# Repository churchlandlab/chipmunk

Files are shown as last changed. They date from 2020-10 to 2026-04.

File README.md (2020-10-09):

# chipmunk

Freely moving auditory and visual discrimination task for mice (adapted from Raposo et al. 2012)

### Introduction

This repo contains code, setup description, assembly instructions and parts design to build a freely moving behavior setup.

The task is a visual and/or auditory accumulation of evidence task. The stimuli is stochastic ticks and/or flashes.

### Description of the setup

[partslist here](partslist.xlsx)
	
There should be a picture here.
	
Here goes a description in words.
	
3d parts for building the setup are in the **custom_parts/3d** folder.
	
The walls are laser cut from *pololu* and the drawings are in the **custom_parts/enclosure**
	
The visual and auditory stimuli printed circuit boards are [here](https://github.com/churchlandlab/SpatialSparrow/tree/dev-couto/pcb/led_panel_split) and can be ordered from *SeeedStudio*.
	
### Software instalation

#### Bpod gen 2

Install Bpod from the repository [here](https://github.com/sanworks/Bpod_Gen2). This was tested with commit `329bd9e`.

### chipmunk task
Clone the repository to `Bpod Local/Protocols`. If you make changes; create a branch and remember to commit changes regularly.

### Calibration 

##### Stimuli

The visual stimuli LEDs response curve should have a plot here.

The auditory speaker response curves were measured with X microphone and a picture should be here.

This needs to be done for every rig? Stored somewhere? Where?

#### Water reward size

Use BPOD to do this. An explanation should be here.

### Behavior monitoring

Cameras wiring for sync is done like this. (Needs diagram.)

Use cameras that have GPIO connections like the FLIR Chamaeleon 3. 
On the Chamaeleon 3 USB you can use the Purple wire (GPIO 2). Connect to BPod to signal trial start and/or end.  To sync multiple cameras use the Green wire and set one of the cameras as master (It is smart to use the same sampling rate). 

Cameras should be set like the following picture. This gives the tracking results with DeepLabCut below (figure).

### Training strategy

Training has 3 phases:

1. Habituation - description of what happens in this phase. How long it lasts. When it ends.

2. Training phase - during these phase mice do the task but only with easy stimuli. This takes around 4 weeks.

3. Testing/experiment phase - mice are now considered experts and difficult stimuli are introduced. Mice perform X above chance.
	
Figure of performance, accross days. Code to produce this figure in the **notebooks** folder

### TODO

Arena size is 20x20cm. An additional chamber can attached to hold an observer.
 
1. walls and floor - laser cut drawings there is an additional 3d part to connect the walls - use transparent red acrylic #2423 from *Pololu*, 6mm. Where can we find small hinges?
2. test the stimuli and put the results in a figure here somewhere. With a description of how to do this.
3. Do we use a sound card?? What the latency? Fixed? How fixed?
4. 3d parts for the ports 2 - adapt the design so that head gear on a mouse is not does not touch the port during licking. Can we do this just with a spout and capacitive sensing?
5. What's in the current port PCB, where the drawing?
6. try different training strategies. Find the best strategy. What the best way to get multimodal enhancement? What is the best loudness and visual saliency? 

Most of these can be done in parallel, some can't. Version 1 can be rough for most of these (we can use code and audio from MudSkipper2 for now.)

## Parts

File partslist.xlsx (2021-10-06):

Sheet: Walls and floor
Part name | Supplier | Catalog number | Price | # parts per rig | Where does it go?
Chipmunk enclosure | Custom pieces |  | 390 | 1
1'' optical post | Thorlabs | TR1 | 4.88 | 3 | Pole to anchor camera to ground plate
8'' optical post | Thorlabs | TR8 | 8.79 | 4 | Legs attaching the ground plate to the floor
2'' optical post | Thorlabs | TR2 | 5.38 | 4 | Camera positioning, 1 each on the groud plate, 2 for the observer side view
1/4"-20 Stainless Setscrew, 1/2", pack of 25 | Thorlabs | SS25S050 | 6.11 | 1 (6 needed) | Fixing the legs and camera posts to the ground plate
Cap screw 8/32 x 1/2'', pack of 50 | Thorlabs | SH8S050 | 7.19 | 1 (4 needed) | Fixing the legs to the floor
Cap screw 1/4''-20 x 3/8'', pack of 50 | Thorlabs | SH8S038 | 6.93 | 1 (2 needed) | Attaching dovetail optical rail to floor and 2'' post to dovetail carrier
Cap screw 8/32 x 1/4'', pack of 50 | Thorlabs | SH8S025 | 6.65 | 1 (2 needed) | Hold demonstrator front and right side wall together with rubber band
Rubber band |  |  |  | 1 | Hold demonstrator front and right side wall together with rubber band
Right-Angle Clamp for Ø1/2" Posts | Thorlabs | RA90/M | 10.05 | 4 | Camera positioning
Dovetail optical rail |  | RLA 0600 | 45.72 | 1 | Observer side view camera adjustment
Dovetail carrier, 1/4'' | Thorlabs | RC1 | 26.94 | 1 | Observer side view camera adjustment
Warm white LED strip | Amazon | B08CDJGRLQ | 36.99 | 1 (~25 cm needed) | Booth lighting

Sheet: Behavioral control
Part name | Supplier | Catalog number | Price | # parts per rig | Where does it go?
Bpod 2 | Sanworks | 1024 | 865 | 1 | Control behavior
Custom nose poke with 8/32 thread on the back |  |  |  | 4 | Nose poke body
19 mm inner spacing ring, 38.2 mm inner diameter (for poke) |  |  |  | 4 | Spacer at the inside of the cage
10 mm outer spacing ring, 38.2 mm inner diameter (for poke) |  |  |  | 4 | Spacer at the outside of the cage
spacer plate |  |  |  | 4 | Additional spacer plate
Nose poke PCB with beam break and LEDS |  |  |  | 4 | Control of beam breaks, LEDs and solenoid valves
Cap screw 8/32 x 1'', pack of 50 | Thorlabs | SH8S100 | 8.27 | 1 (8 needed) | Attaches nose poke PCB to the poke on the outside of the cage
Washer #8, pack of 100 | Thorlabs | W8S038 | 3.59 | 1 (8 needed) | Between screw head and PCB
Haxagonal nylon standoff for 8/32 screws, pack of 10 | Grainger | 3XYN9 | 2.92 | 1 (8 needded) | To attach PCB above the spacer plate
Teensy 3.2 | Adafruit | 2756 | 19.95 | 1 | Control of the beam break for the observer deck
Perma-proto half-sized breadboard | Adafruit | P1609 | 4.5 | 1 | Bread board for observer deck control
Teensy shield | Sanworks | 1023 | 32 | 1 | Connect teensy to Bpod
3 mm infrared LED | Mouser | 696-OED-EL-8L | 0.4 | 1 | Observer deck beam break
3 mm photodiode | Mouser | 710-1540031EC4590 | 0.65 | 1 | Observer deck beam break
47 Ohm resistor, 1/4 W | Mouser | 603-CFR-25JT-52-47R | 0.1 | 1 | Resistor between 5V input and LED
1 MOhm resistor, 1/4 W | Mouser | 588-OK1055E-R52 | 0.13 | 1 | Resistor between diode readout and ground
Solenoid valve | The Lee Company | LHDA1233115H |  | 4 | Control of water dispensing
Silicone valve cap, pack of 50 | Amazon | B08H5TT689 | 5.99 | 1 (4 needed) | Control of water dispensing
Silicone tubing | Grainger | 9WDF5 | 76.3 | 1 (~2 m needed) | Water delivery
Female luer to hosebarb adapter | Masterflex | HV-30800-08 | 11.8 | 25 (8 needed) | Couple syringe and needle to tubing for water dispensing
18G 2'' needle | Amazon | B07Y2HYBDG | 15.99 | 1 (4 needed) | Deliver water throught the poke
60 ml syringe with luer lock | Amazon | B07P53ZTWN | 9.99 | 1 (4 needed) | Water reservoir
Small acrylic plate (for instance 5 x 3 cm), left over from custom cutting |  |  |  | 2 | Attach solenoid valves with M2 screws
M2 x 8 mm screw, philips head | Grainger | 31JR96 | 4 | 1 (6 needed) | Attach solenoid valves with M2 screws
Velcro tape | Amazon | B00FQ937NM | 7.78 | 1 (~20 cm needed) | Tape plates with solenoids and syringes to the booth wall
6.5 mm spacer tubing, 4.3 mm inner diameter for 8/32 x 1/4'' |  |  |  | 8 | Part of the nose poke

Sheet: Visual and auditory stimuli
Part name | Supplier | Catalog number | Price | # parts per rig | Where does it go?
LED flashboard master with cold white 48 LED array | ALA Scientific | ALA-Flash-M-01 |  | 1 | PCB to control LED flashing, one of two LED arrays to be axtracted for the stimulus presentation
Cold white 48 LED array, pack of 6 | Amazon | B00IZCMYB8 | 12.99 | 1 (1 extra needed in addition to the Ala board | Extract the other LED array for the stimulus presentation
3.5 mm stereo jack to female to RCA male connector | Amazon | B06XYCTRP9 | 6.99 | 1 | Feed visual signal from sound card into the flashboard PCB
RCA female to BNC male connector | Amazon | B005B4O4GG | 0.7 | 1 | Feed visual signal from sound card into the flashboard PCB
Haxagonal nylon standoff 0.5'' for 8/32 screws, pack of 10 | Grainger | 3XYN9 | 3.88 | 1 (4 needed) | Spacer between the plate holding LED flashboards and the translucent white window in the back wall of the demonstrator
Stereo speakers, active | Harmon/Kardon (discontinued) Logitech |  |  | 1
3.5 mm stereo Audio Cable Extension Male to Male | Amazon | B07QF1VRPB | 5.99 | 1 | Connect speaker to computer
3.5 mm stereo jack female to female connector | Amazon | B002N1XN4E | 3.99 | 1 | Connect speaker to computer

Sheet: Video tracking
Part name | Supplier | Catalog number | Price | # parts per rig | Where does it go?
Chameleon3 high-speed camera, 172'' sensor | FLIR | CM3-U3-13Y3M-CS | 369 | 3 | Cameras for demonstrator and observer bottom view and observer side view
JST GPIO Connector for Chameleon 3 | FLIR | ACC-01-3013 | 10 | 3 | Synchronize camera acquisition to Bpod trials and synchronize the 3 cameras together
USB3.1 locking cable | FLIR | ACC-01-2300 | 10 | 3 | Connect cameras to computer
Tripod adapter for Chmeleon3 | FLIR | ACC-01-0003 | 5 | 3 | Attach camera to optical post to anchor it on the ground plate or floor
Fujinon 1.5 MP 6mm lens | B & H photo | FUDF6HA1S | 132 | 1 | Observer side view objective
Fujinon CS mount varifocal lens, mannual iris | discontinued | YV4.3X2.8SA-2 | ~90 | 2 | Demonstrator and Observer bottom view, first choice
Computar CS-Mount 2.8-12mm Varifocal Lens, (could be better) | B & H photo | COZ2813CSIR2 | 52 | 2 | Demonstrator and Observer bottom view, alternative
(Adapter with External M27 x 0.5 Threads and Internal SM1 Threads | Thorlabs | SM1A36 | 21.86 | ev. 1 | This piece should be mountable to the outside of the Fujinon DF6HA-1S objectives (M27 x 0.5 mm) and may hold a 25 mm colored glass filter (using a SM1M05 ring

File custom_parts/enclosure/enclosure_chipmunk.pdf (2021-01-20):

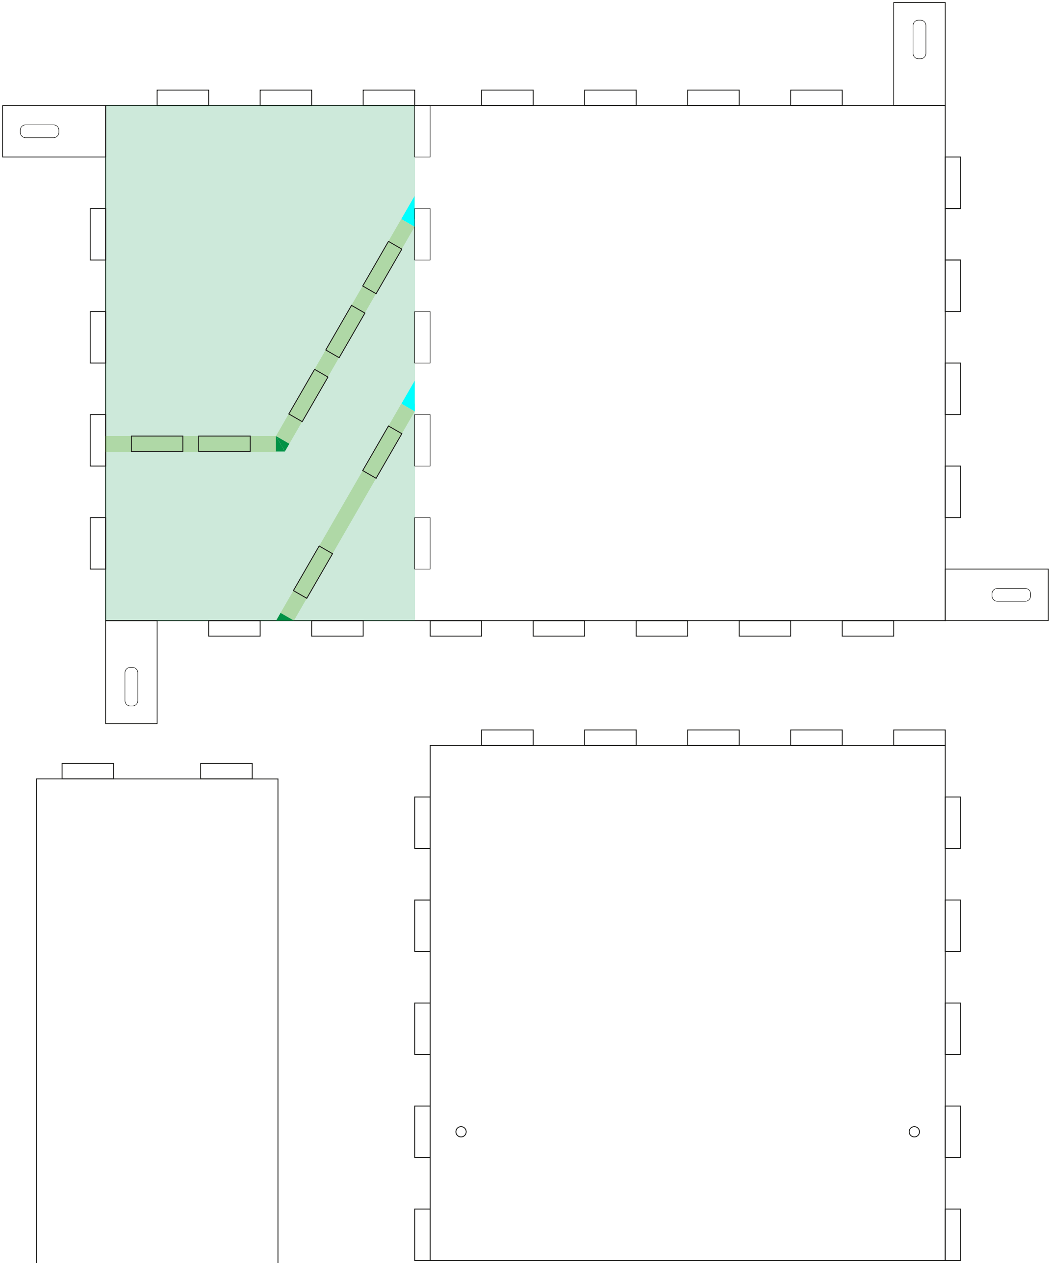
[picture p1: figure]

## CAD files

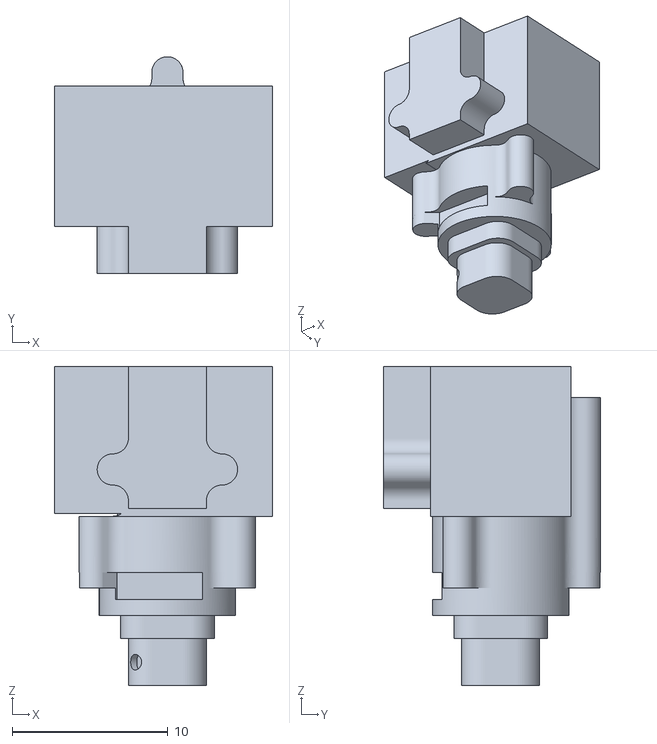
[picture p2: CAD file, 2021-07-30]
custom_parts/3d/MiniscopeV4Dummy.stl
14.0 x 13.9 x 20.5

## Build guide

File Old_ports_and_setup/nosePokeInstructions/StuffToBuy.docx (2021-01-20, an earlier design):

for the photosensors. I'm not sure which parts, i.e. part number used, but the following should work:

- mouse : 875nm IR emitter (SIR-234, Digikey# 1080-1172-ND (http://www.digikey.com/product-detail/en/SIR234/1080-1172-ND/2675663)) and 880nm IR phototransistor (SFH 310 Digikey # 475-1444-ND (http://www.digikey.com/product-detail/en/SFH%20310%20FA-2/3/475-1444-ND/1228087)), 3mm each)

- rat: 940 nm IR emitter (IR204C-A, Digikey # 1080-1077-ND (http://www.digikey.com/product-search/en?mpart=IR204C-A&vendor=1080)) and 940nm phototransistor ( LTR-4206, Digikey # 160-1988-ND (http://www.digikey.com/product-detail/en/LTR-4206/160-1988-ND/214965)), 3mm each

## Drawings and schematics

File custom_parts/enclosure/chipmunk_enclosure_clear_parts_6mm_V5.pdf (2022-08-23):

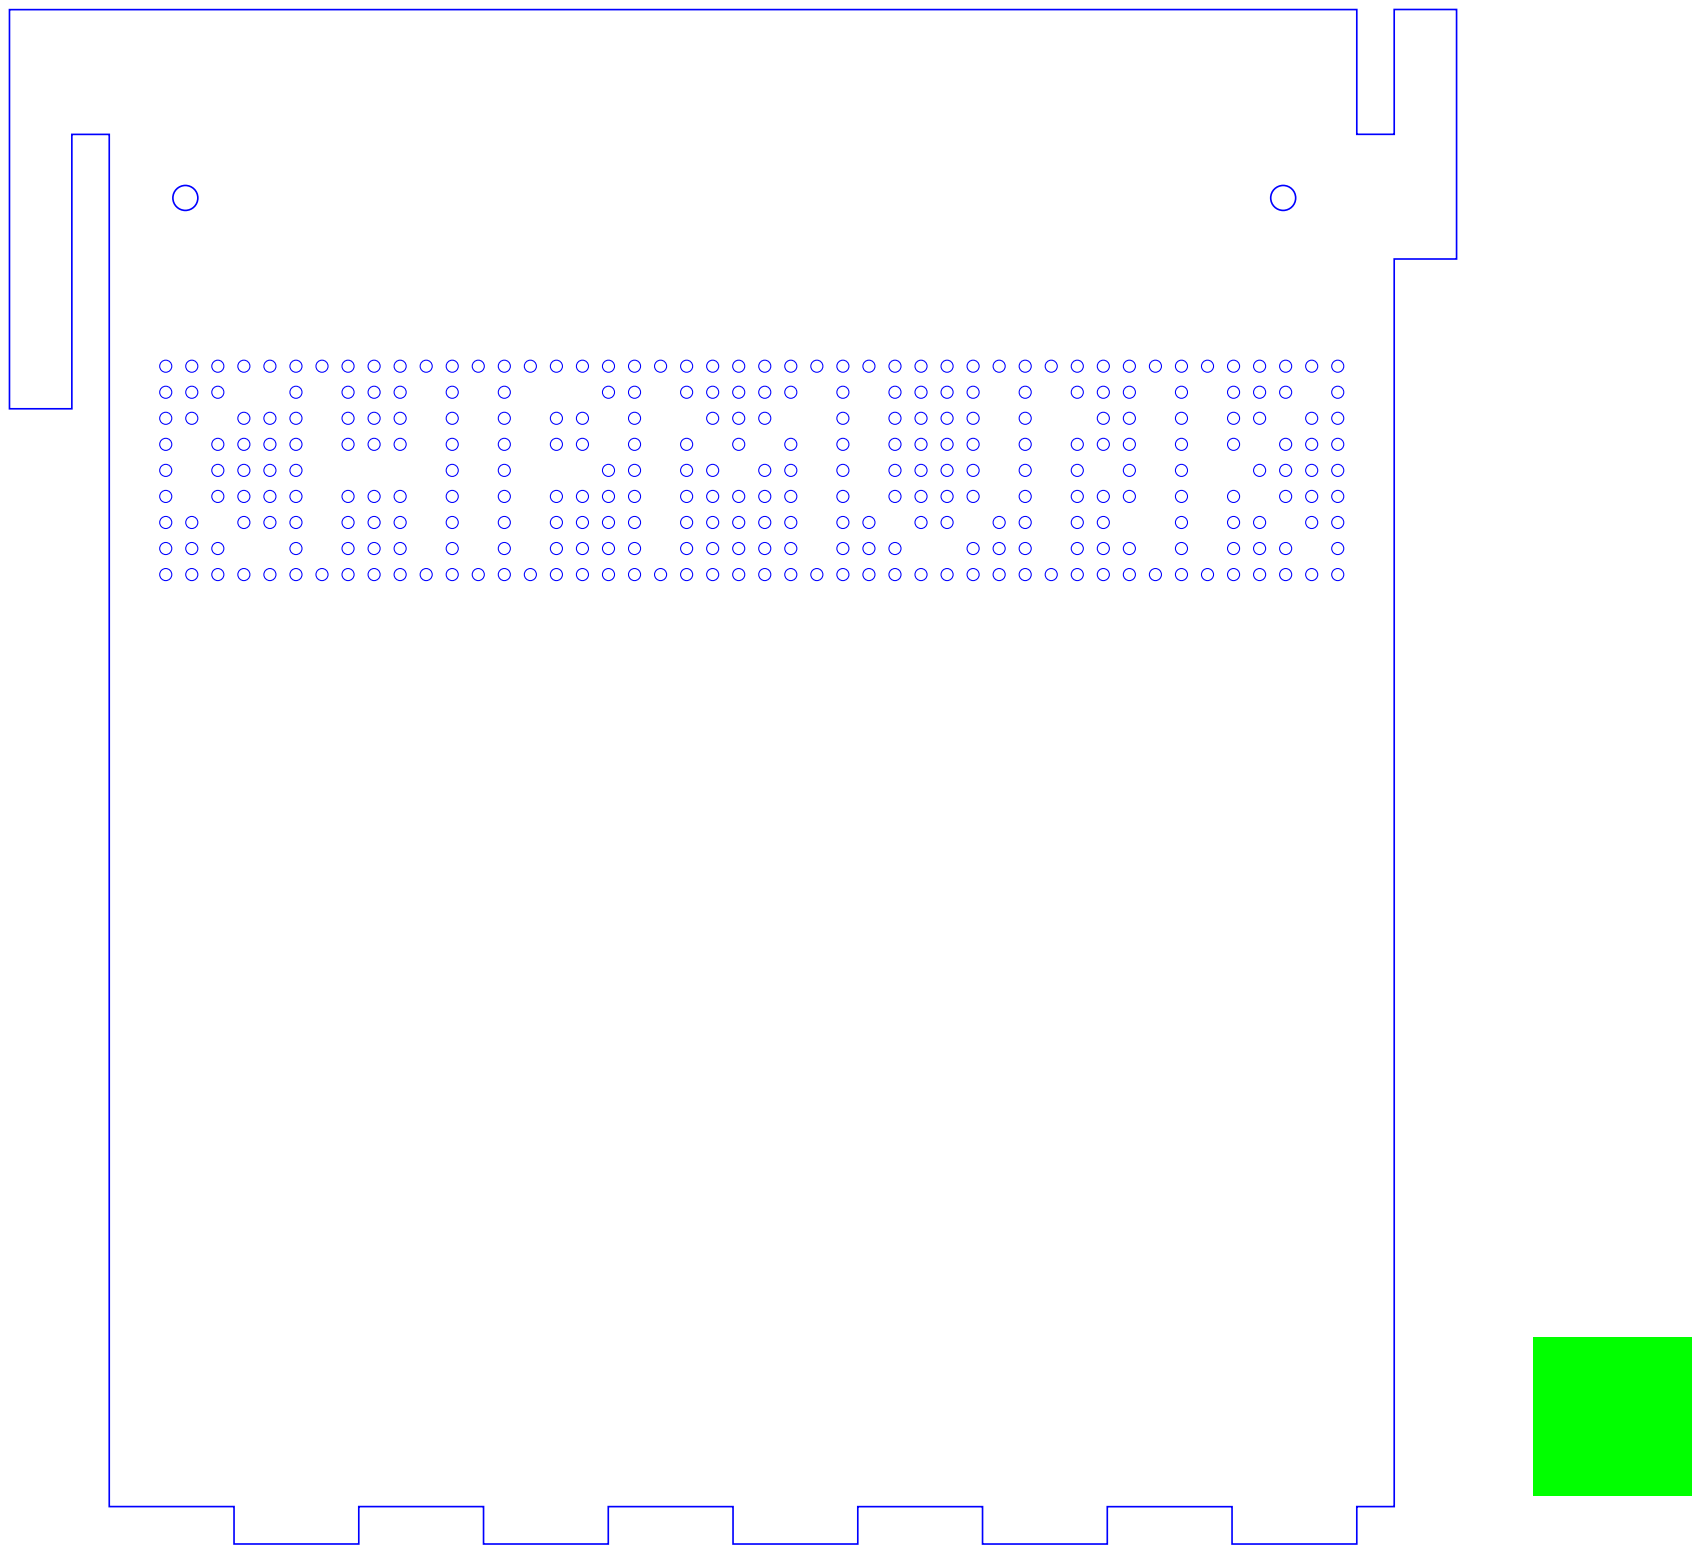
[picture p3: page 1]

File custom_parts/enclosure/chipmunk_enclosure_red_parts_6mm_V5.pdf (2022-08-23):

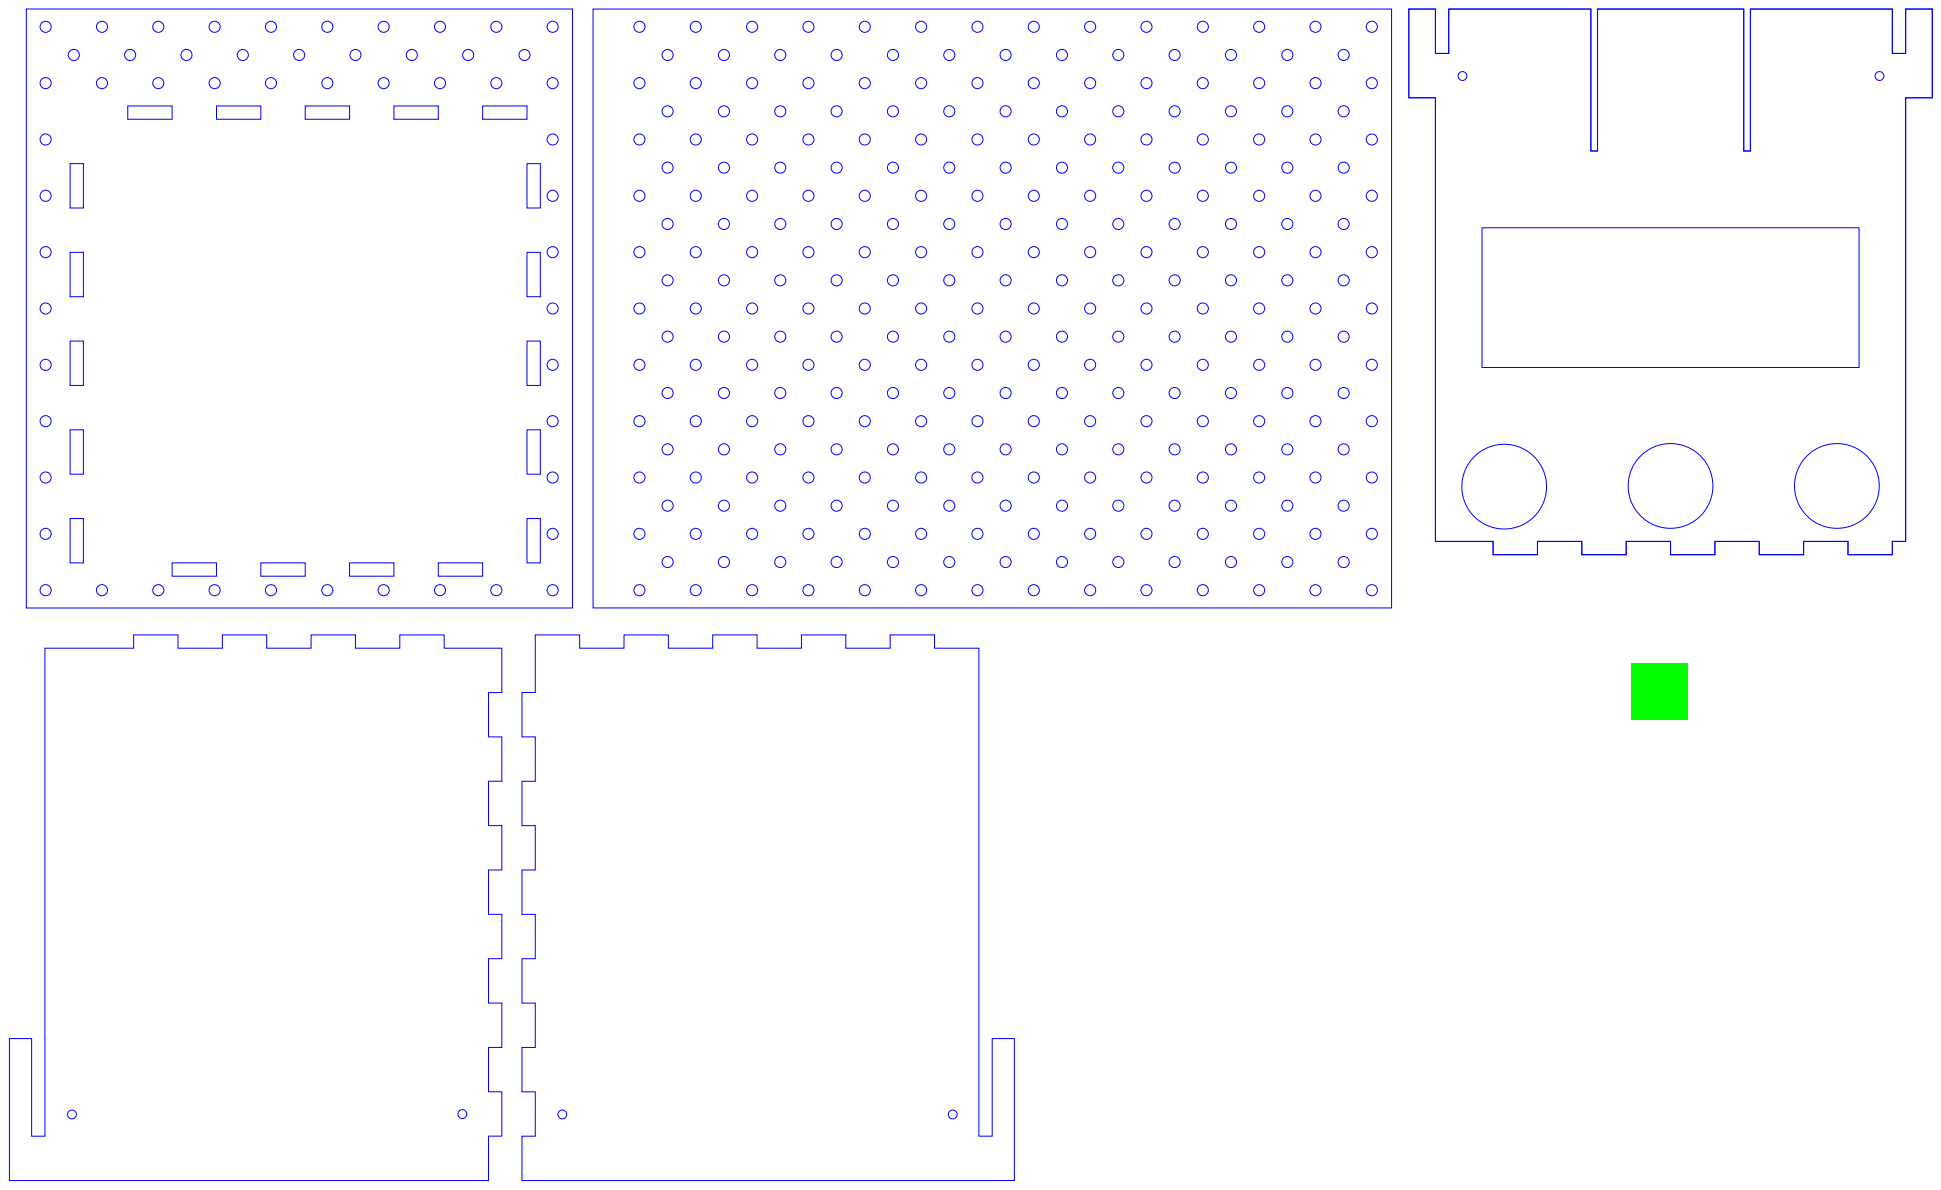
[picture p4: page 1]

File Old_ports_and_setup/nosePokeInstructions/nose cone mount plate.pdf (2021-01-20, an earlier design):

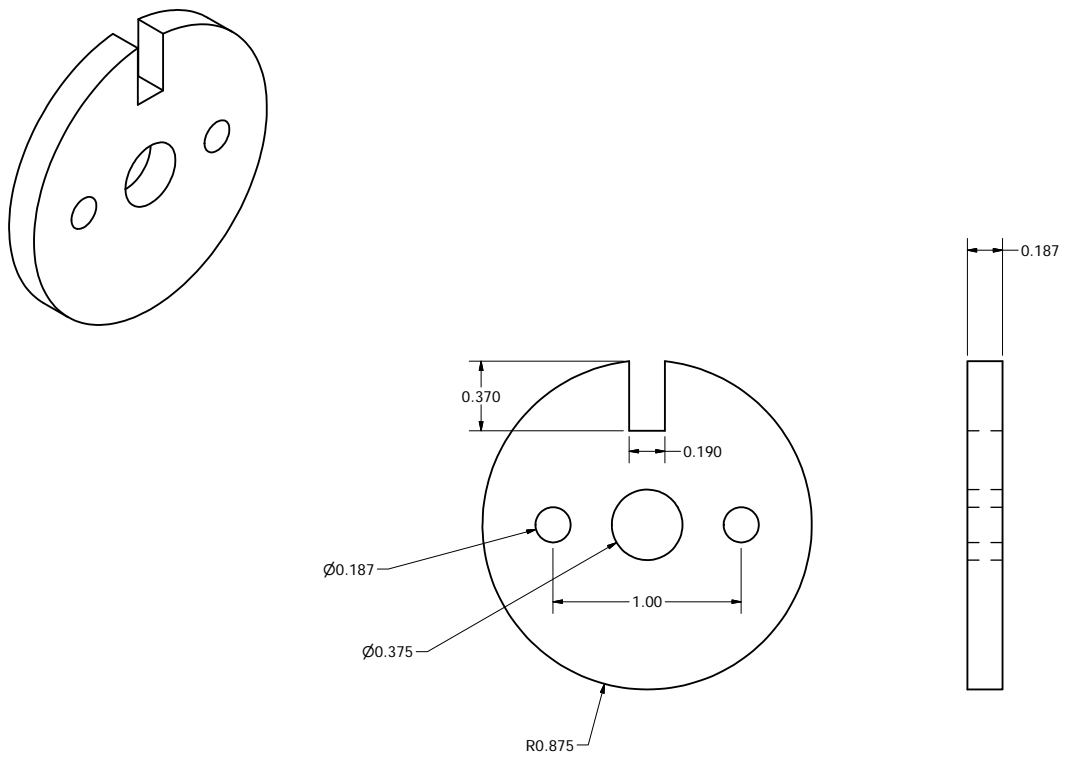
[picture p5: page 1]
TITLE

DRAWN eifert | 6/24/2013

CHECKED

MFG

APPROVED

SIZE C | DWG NO nose cone mount plate | REV

SCALE | | SHEET 1 OF 1

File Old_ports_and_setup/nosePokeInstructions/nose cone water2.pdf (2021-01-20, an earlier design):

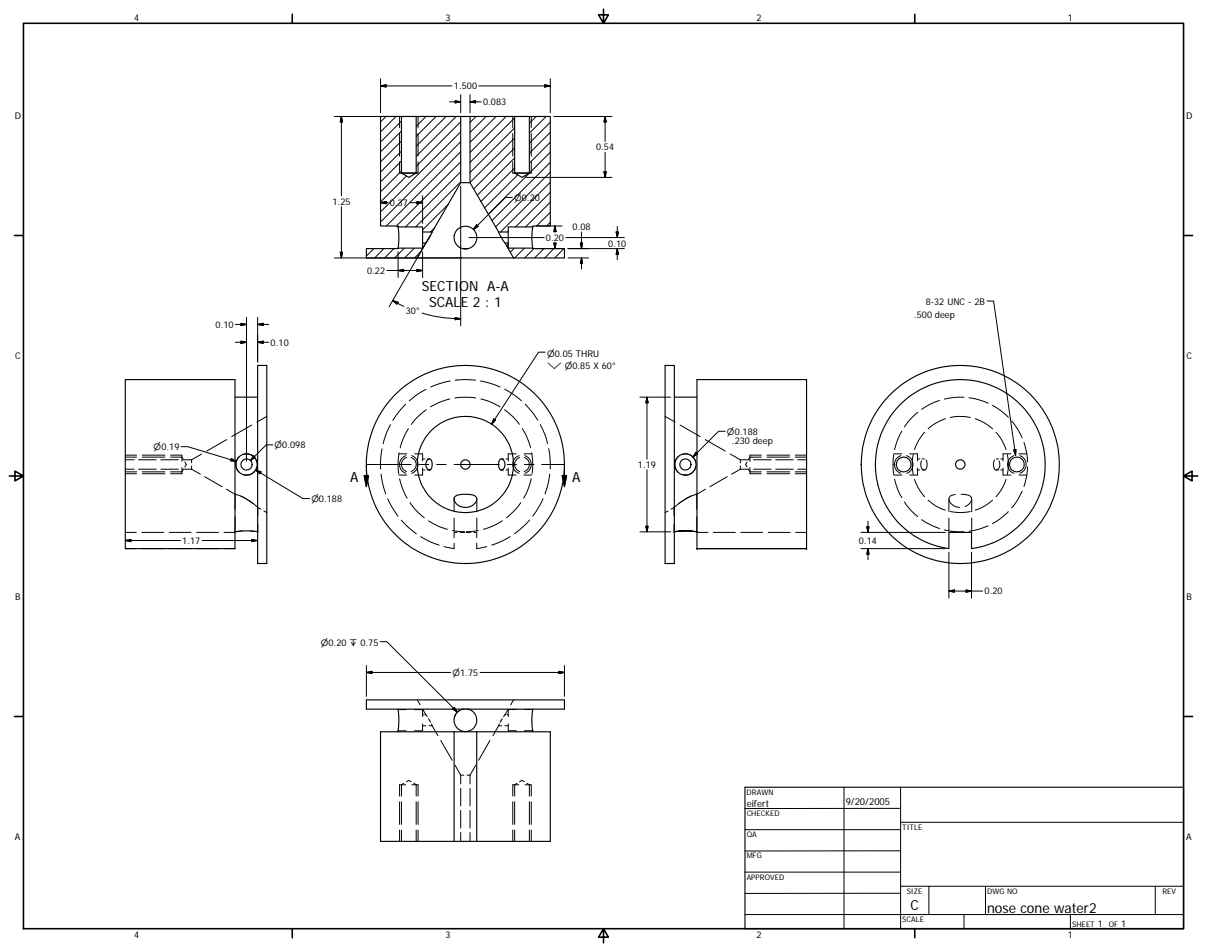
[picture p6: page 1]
SECTION A-A SCALE 2 : 1; TITLE; 8-32 UNC - 2B; n0.05 THRU w n0.85 X 60°; n0.188 .230 deep; .500 deep

DRAWN eifert | 9/20/2005

CHECKED

MFG

APPROVED

SIZE C | DWG NO nose cone water2 | REV

SCALE | | SHEET 1 OF 1

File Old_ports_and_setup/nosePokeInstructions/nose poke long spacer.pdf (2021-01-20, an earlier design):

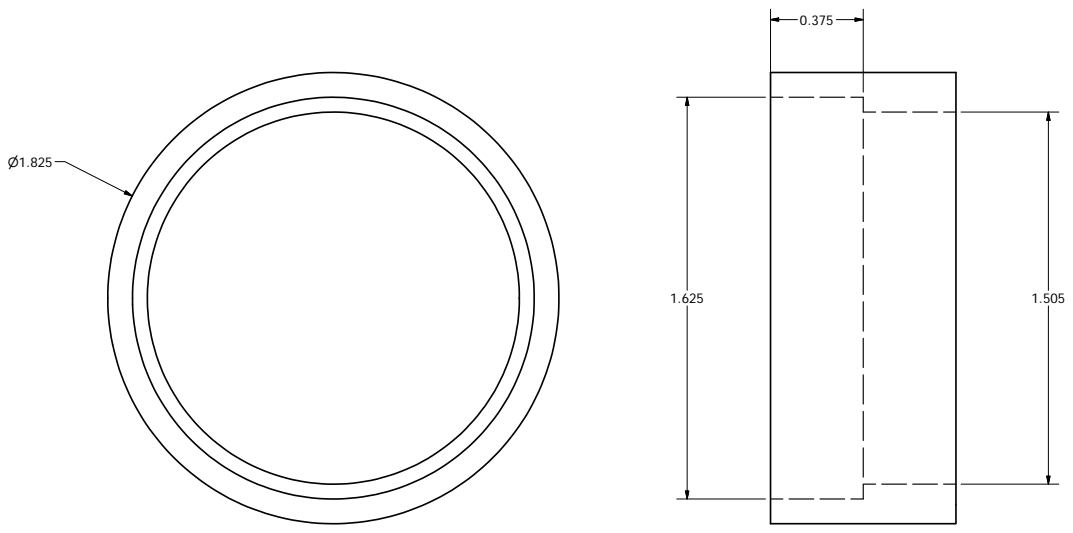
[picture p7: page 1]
TITLE

DRAWN eifert | 9/9/2015

CHECKED

MFG

APPROVED

SIZE C | DWG NO | REV

SCALE | | SHEET 1 OF 1

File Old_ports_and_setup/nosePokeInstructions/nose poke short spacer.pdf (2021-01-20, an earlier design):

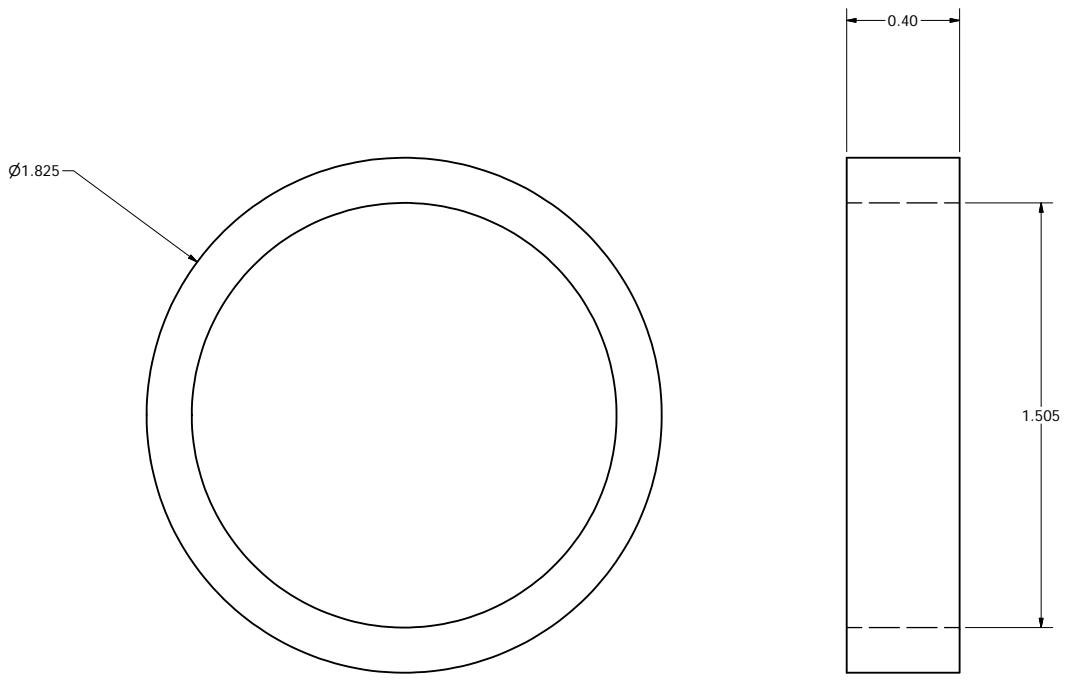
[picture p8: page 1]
TITLE

DRAWN eifert | 9/9/2015

CHECKED

MFG

APPROVED

SIZE C | DWG NO nose poke short spacer | REV

SCALE | | SHEET 1 OF 1

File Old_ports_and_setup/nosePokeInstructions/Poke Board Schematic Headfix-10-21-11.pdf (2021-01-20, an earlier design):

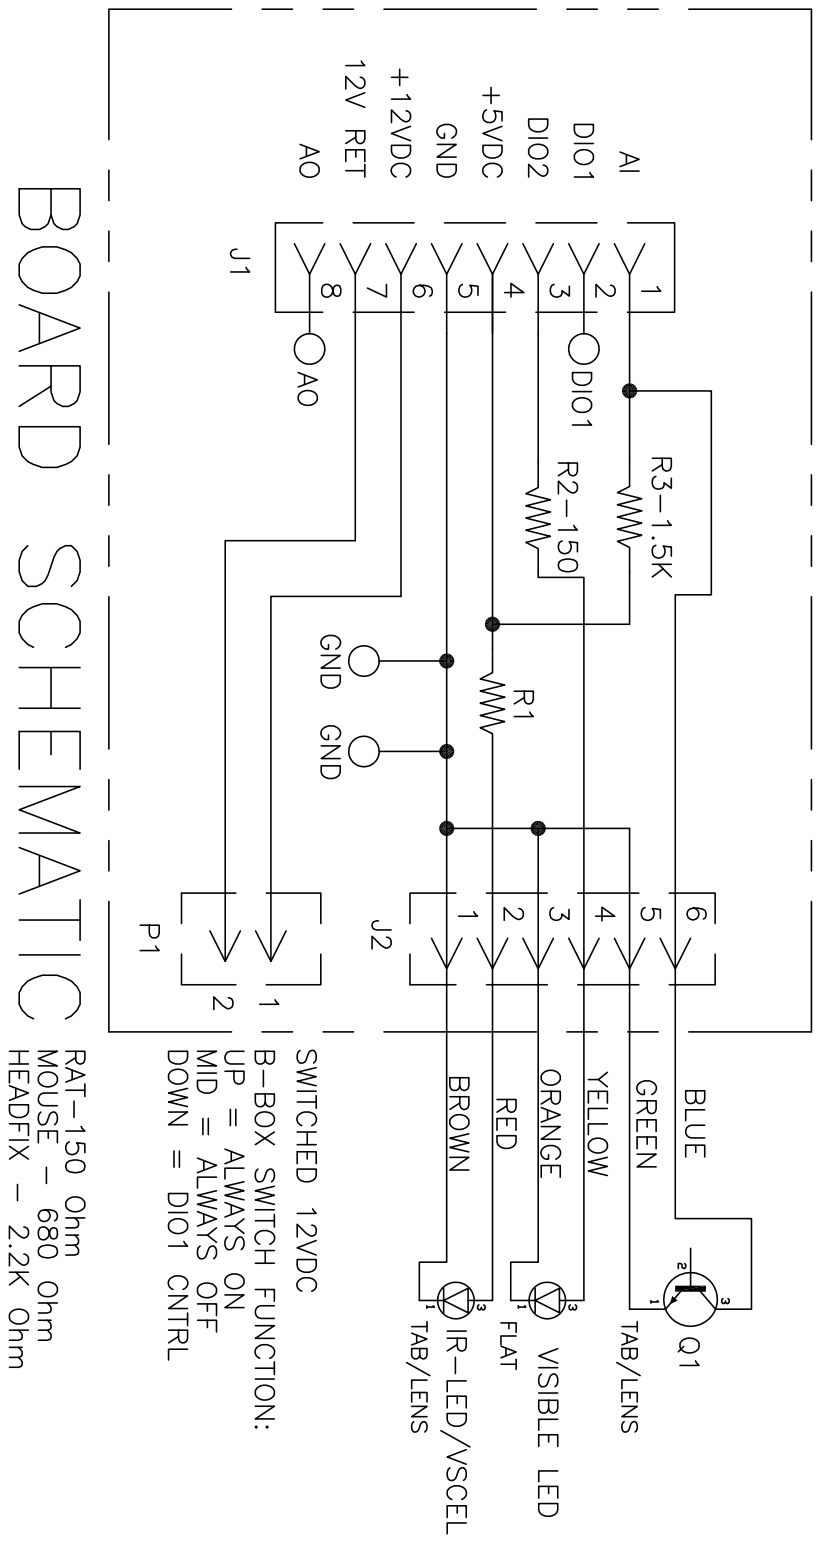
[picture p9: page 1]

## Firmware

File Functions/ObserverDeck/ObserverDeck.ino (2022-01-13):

//Use serial connection to send byte-encoded information between Bpod and Teensy.
//Incoming bytes are processed on pin 0 and outgoing ones on pin 1. All the other pins are freely configurable.
//Once programmed, Teensy can be supplied with power via the ethernet connection.
//
//This code lets Teensy report beam breaks as events to Bpod. In parallel Bpod can request to start counting
//beam breaks until it receives a stop signal and reports the number of beam breaks that occured during
//the counting period.

// Include the Teensy shield code
#include "ArCOM.h"

// Serial-write variables
unsigned long FirmwareVersion = 2;
char moduleName[] = "ObserverDeck"; // Name of module for manual override UI and state machine assembler
ArCOM Serial1COM(Serial1); // UART serial port

#define START_COUNTING 30 // Define the serial input messages for different bytes
#define STOP_COUNTING 31
#define REPORT_COUNT 32
#define NO_INITIATION_RECORDED 33 //Observer initiation window has passed
#define SEND_MODULE_INFO 255

#define BEAM_BROKEN 1 // Define the serial output messages for different bytes
#define BEAM_JOINED 2
#define OBSERVER_FIXATION_SUCCESS 3
#define OBSERVER_FIXATION_FAIL 4
#define OBSERVER_NO_INITIATION 5
#define UNDEFINED_INPUT_SENT 15

//---------Pin configuration--------------------//

#define BeamBreakReadoutPin 14 // Lets Teensy read from this pin

//----------Set up the serial sampling and pin mode-------//
void setup() {
  //Set the refreshing frequency
  Serial1.begin(1312500); // ethernet baud rate from Bpod
  Serial.begin(9600); // USB baud rate
  
  //Configure pin
  pinMode(BeamBreakReadoutPin, INPUT_PULLDOWN);
  // This pin has to be set to PULLDOWN because it would accumulate charges otherwise and 
  // not report the beam breaks anymore after the first one. Due to the PULLDOWN the input voltage
  // should be a bit higher. Here, rather than the 3.3 V power pin the direct USB/Ethernet 
  // power source is used that comes at ~5 V.
  attachInterrupt(digitalPinToInterrupt(BeamBreakReadoutPin),beamBreakEvent, CHANGE);
  // Set up the beam break readout pin as an interrupt that executes beamBreakEvent upne every change
  // in the beam state.
  }

  // Set up the communication variables
  int nBytes = 0; // Number of incoming bytes
  int serialInputInfo; // The input instruction

  // Readout and count
  //int beamJoined = 0; //Track the number of times the beam was unbroken!
  volatile int countUnbroken = 0; // Count how many times the beam was joined again after having been broken once (to initiate observation).
  volatile bool beamState = 1;
  //int previousBeamState = 0; // Detect change in the beam state compared to prior state
  volatile bool doCounting = 0; // Boolean to check whether events need to be counted
  bool notInitiated = 1; // Boolean to see whether the observer initiated a trial,
  //Start with true here, because if the demonstrator fails before the observer gets the chance that is also a non initiation.

void serialEvent1(){
// Only try reading bytes when they are available 
serialInputInfo = Serial1COM.readByte(); // For some reason one needs to refer to SerialCOM1 here rather than Serial1.
////--------Checking---------/////
     Serial.print("serialInputInfo: ");
     Serial.println(serialInputInfo); //If connected via USB report the input info in the serial viewer
     Serial.print("\n");
     ////////////////////////////////////
      
     switch (serialInputInfo) { // Check the input information
            case SEND_MODULE_INFO:
            returnModuleInfo();
            break;
  
            case START_COUNTING:
            doCounting = 1;
            notInitiated = 0; //Reset this variable at each new trial
            countUnbroken = 0; //This is important because stuff might happen before...
            break;

            case STOP_COUNTING:
            doCounting = 0;
            break;

            case NO_INITIATION_RECORDED:
            notInitiated = 1;
            break;

            case REPORT_COUNT:
            if (notInitiated == 1) {
              Serial1.write(OBSERVER_NO_INITIATION);
            } else {
              if (countUnbroken == 0) { // Send either success or fail back to Bpod
                 Serial1.write(OBSERVER_FIXATION_SUCCESS);
              } else {
                  Serial1.write(OBSERVER_FIXATION_FAIL); 
              }
            }
            
              ////----Checking-------/////
              Serial.print("Number of times beam joined: ");
              Serial.println(countUnbroken); // If connectd to USB report number of unbreakings
              Serial.print("\n");
              ////------------------////

              notInitiated = 1; //Assume again no initiation to be the default unless teensy is asked to start counting
              break;
              
              default:
              break;
      }
}

void loop() {
  /*  // Check for changes in the beam state
    beamState = digitalRead(BeamBreakReadoutPin); //Get the current beam break state
    if (beamState != previousBeamState) {
      if (beamState == 0) {
        Serial1.write(BEAM_BROKEN);
        Serial.print("Beam broken");
        Serial.print("\n");
        /////////////////
      }   else if (beamState == 1) {
        Serial1.write(BEAM_JOINED);
        countUnbroken++; //Do the actual counting
        ////-----Checking--------/////
        Serial.print("Beam joined");
        Serial.print("\n");
        ////////////////
      }
      previousBeamState = beamState;
      
    } */
}

///-------------Interrupt function for the beam break events------------------///
void beamBreakEvent(){
  beamState = digitalRead(BeamBreakReadoutPin); //Get the current beam break state
  if (beamState == 0) {
        Serial1.write(BEAM_BROKEN);
        Serial.print("Beam broken");
        Serial.print("\n");
      }   else if (beamState == 1) {
        Serial1.write(BEAM_JOINED);
        Serial.print("Beam joined");
        Serial.print("\n");
      if (doCounting == 1){
        countUnbroken++; //Do the actual counting if required
        }
      }
}

///-------Define the module info return function----------------//
void returnModuleInfo() {
  Serial1COM.writeByte(65); // Acknowledge
  Serial1COM.writeUint32(FirmwareVersion); // 4-byte firmware version
  Serial1COM.writeByte(sizeof(moduleName) - 1); // Length of module name
  Serial1COM.writeCharArray(moduleName, sizeof(moduleName) - 1); // Module name
  Serial1COM.writeByte(0); // 1 if more info follows, 0 if not
}

///////////////////////////////////////////////////////////////////////////////////////////

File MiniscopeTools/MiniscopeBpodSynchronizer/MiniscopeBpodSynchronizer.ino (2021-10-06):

/*
Teensy code to synchronize the miniscope square pulses (each orientation change indicates
an acquired frame) and the output from a Bpod BNC (set to high at the beginning of 
each trial). Run syncMiniscopeToBpod.py to generate a synchronization log file
(.mscopelog). Frames and trial events are recorded as:
Recording pin, frame/trial number, timestamp (in miliseconds)

This program first reset the frame and trial counts when receiving the serial input
string '1' (= 49). Then incoming frames and trial events will be logged using the
respective interrupts. At the end when string '0' (=48) arrives the output of the
will be interrupted.
LO, 8/5/2021
*/

#include "TimeLib.h" //To get millis()

#define MINISCOPE 2
#define BPOD 23
#define FINDINTACT 11
#define TESTMINI 10

// Set up the required variables
volatile unsigned long frameNumber = 0; //Counts the number of frames acquired from the miniscope
volatile unsigned long long timeStamp = 0; //Assigns a timestamp in milisceonds from the start of the
//acquired frame from the miniscope or the trial event.
volatile bool trialStartFlag = 0; //Flag for trial start versus stop
volatile unsigned long trialNumber = 0; //Count trial number
volatile bool initialized = 0; //Jumps to true once the frames have been reset and the header is sent
int serialMessage = -1; //Message from the python function to enable counting or stoppining it.


////////////////////
//Checking
bool frameSimulation = 0; //simulated miniscope frame square wave
///////////////////

///-----Setup function for interrupts-------------///
void setup() {
  Serial.begin(9600);

  //Configure pins
  pinMode(MINISCOPE, INPUT); //Set the miniscope sync signal to input
  pinMode(BPOD, INPUT); //Set the Bpod trial start/stop signal to input

 /////////////////////
 //For testing
  pinMode(TESTMINI, OUTPUT); //Generate regular TTL pulses
  ////////////////////
 
  //Set the interrupts
  attachInterrupt(digitalPinToInterrupt(MINISCOPE), miniscopeFrame, CHANGE);
  //Use digitalPinToInterrupt for compatibility with other arduino devices
  attachInterrupt(digitalPinToInterrupt(BPOD), BpodTrialEvent, CHANGE);
  }

///--------Leave empty for experiment, uncomment for checking------///
void loop() {
  /////////////////////////////
  //Testing 
  /*frameSimulation = digitalRead(MINISCOPE);
  Serial.write("Miniscope pulse state is: ");
  Serial.println(frameSimulation); 
  */
  //digitalWrite(TESTMINI, HIGH);
  //delay(1000);
  /*
  frameSimulation = digitalRead(MINISCOPE);
  Serial.write("Miniscope pulse state is: ");
  Serial.println(frameSimulation);

  Serial.write("Bpod state is: ");
  Serial.println(frameSimulation);
  */
  //digitalWrite(TESTMINI, LOW); 
  //delay(1000);
}

///-------Interrup function for miniscope frame capturing and serial output-----------///
void miniscopeFrame(){
  if (initialized){
    frameNumber++; //Add this frame to the number log
    timeStamp = millis(); //Get a timestamp for the incoming frame
    Serial.printf("%d,%lu,%llu\n", MINISCOPE, frameNumber, timeStamp);
  }
}

///-----Interrupt function for Bpod trial event info------///
void BpodTrialEvent(){
  if (initialized){
    timeStamp = millis(); //Get the time stamp for the trial event
    trialStartFlag = trialStartFlag == 0; //Switch the state of the logic variable
    if (trialStartFlag) {
      trialNumber++; //If this is a trial start go to the next trial number
      Serial.printf("%d,%lu,%llu\n",BPOD, trialNumber, timeStamp);
    //} else {
   //  Serial.printf("# %lu,%llu - trial_end: %lu\n",frameNumber, timeStamp, trialNumber);
    }
  }
}

///------Get instructions from syncMiniscopeToBpod.py---------///
void serialEvent() {
  serialMessage = Serial.read();

  //Reset the trial variables when a serial input arrives
  if (serialMessage == 49) {
  frameNumber = 0;
  timeStamp = 0;
  trialNumber = 0;
  trialStartFlag = 0;

  //Write the pin specs to the header
  Serial.printf("Reset frame and trial count. Miniscope channels is: %d and Bpod channel is: %d\n", MINISCOPE, BPOD);
  Serial.println("channel, eventNumber, teensyTime"); //println automatically inserts a line break at the end of the string
  initialized = 1;
  } else if (serialMessage == 48) {
    initialized = 0;
  }
}

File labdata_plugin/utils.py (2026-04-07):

from labdata.utils import *
import warnings

def load_chipmunk_trialdata(file_name):
    '''Read the behavioral data from .mat or .obsmat and return a
    pandas data frame with the respective data for each trial
    Parameters
    ----------
    file_name: string, path to a chipmunk .mat or .obsmat file
    Returns
    -------
    trialdata: pandas data frame, data about the timing of states and events, choices and outcomes etc.
    Examples
    --------
    trial_data = load_chipmunk_trialdata(file_name)

    Port1 - 'left'
    Port2 - 'center'
    Port3 - 'right'
    '''
    import os
    import pandas as pd
    from scipy.io import loadmat
    import numpy as np
    metadata = None
    try:
        sesdata = loadmat(file_name, squeeze_me=True,
                              struct_as_record=True)['SessionData']
        if 'Notes' in sesdata.dtype.names:
            notes = sesdata['Notes']
            notes = '\n'.join([f'trial:{itrial};{note}' for itrial,note in enumerate(notes.tolist()) if len(note)])
        else:
            notes = ''
        tset = sesdata['TrialSettings'].tolist()
        if 'rigNo' in  tset.dtype.fields:
            setup_name = tset['rigNo'][0]
        else:
            setup_name = None
        if 'researcher' in  tset.dtype.fields:
            experimenter = tset['researcher'][0]
        else:
            experimenter = None
        if 'demonWeight' in tset.dtype.fields:
            weight = tset['demonWeight'][0]
        else:
            weight = np.nan
            
        metadata = dict(notes = notes,
                        setup_name = setup_name,
                        experimenter = experimenter,
                        weight = weight)
        
        tmp = sesdata['RawEvents'].tolist()
        tmp = tmp['Trial'].tolist()
        uevents = np.unique(np.hstack([t['Events'].tolist().dtype.names for t in tmp])) #Make sure not to duplicate state definitions
        ustates = np.unique(np.hstack([t['States'].tolist().dtype.names for t in tmp]))
        trialevents = []
        trialstates = [] #Extract all trial states and events
        for t in tmp:
             a = {u: np.array([np.nan]) for u in uevents}
             s = t['Events'].tolist()
             for b in s.dtype.names:
                 if isinstance(s[b].tolist(), float) or isinstance(s[b].tolist(), int):
                     #Make sure to include single values as an array with a dimension
                     #Arrgh, in the unusual case that a value is an int this should also apply!
                     a[b] = np.array([s[b].tolist()])
                 else:
                        a[b] = s[b].tolist()
             trialevents.append(a)
             a = {u:None for u in ustates}
             s = t['States'].tolist()
             for b in s.dtype.names:
                     a[b] = s[b].tolist()
             trialstates.append(a)
        trialstates = pd.DataFrame(trialstates)
        trialevents = pd.DataFrame(trialevents)
        trialdata = pd.merge(trialevents,trialstates,left_index=True, right_index=True)
        ## Insert a column for DemonWrongChoice in trialdata if necessary
        #if 'DemonWrongChoice' not in trialdata.columns:
        #    trialdata.insert(trialdata.shape[1], 'DemonWrongChoice', [np.array([np.nan, np.nan])] * trialdata.shape[0])
        #Add response and stimulus train related information: correct side, rate, event occurence time stamps
        trialdata.insert(trialdata.shape[1], 'response_side', sesdata['ResponseSide'].tolist())
        trialdata.insert(trialdata.shape[1], 'correct_side', sesdata['CorrectSide'].tolist())
        #Get stim modality
        tmp_modality_numeric = sesdata['Modality'].tolist()
        if isinstance(tmp_modality_numeric[0], str): #In some early recordings a string value was assigned to the modality
            for k in range(tmp_modality_numeric.shape[0]):
                if tmp_modality_numeric[k] in ['visual', 'Visual']:
                    tmp_modality_numeric[k] = 1
                if tmp_modality_numeric[k] in ['audio', 'auditory', 'Auditory']:
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

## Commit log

2020-10-08 Added partslist skeleton
    [partslist.xlsx]
2020-10-09 Added material suggestion to walls.
2020-10-09 Hinges to todo
2020-10-09 Draft of the enclosure without hinges
2020-10-22 Size of the parameter window. Support autorun mode where the stim starts without nose poke. camera starts recording after update settings is pressed. BNC state 1 during PlayStimuli.
2020-11-29 New enclosure laser cut parts (draft without merge)
2020-11-29 Merged enclosure junctions.
2020-12-01 Changes to the enclosure: Added side walls of the observer chamber, corrected hole spacing in the floor and rig floor, added space on the floor to anchor port wall to the floor. In this version the o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
2020-12-02 Chipmunk enclosure modification: Merged individual parts where necessary for laser cutting.
2021-01-27 Added code to copy the generated files to a network drive when terminating chipmunk. Currently the drive is hard coded to be mounted on Z, see line 44.
2021-02-07 Transient fix: Added WhiteNoiseCalibration to Bpod Local\Calibration Files and included some lines to access the calibration file from there instead of dropbox. Changed redundant part of generateAndU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
2021-04-20 MAJOR restructuring! Added antiBias functions, random delay generator, stimulus modality and rate assignmet and stim train generation functions. As a new feature each state matrix has its own assembl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
2021-06-04 MAJOR restructuring of chipmunk. Updated retrieval of trial information, included try catch statement to save behavioral data when chipmunk crashes, implementation debugged for self-initiated demonst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
    [partslist.xlsx]
2021-06-05 Fixed chipmunk for labcams, modified the file copying to remote location; added a new state in the DemonstratorSelfInititatedTask assembler function to stop playing the stimulus when the animal withd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
2021-06-08 Packaged LED switch into a function, fixed bugs in retrieveTrialData and chipmunk, corrected the valve opening time (coupled to the DemonReward state) inside the fixation self and paced smaAssemblers.
2021-06-29 Included the folder ObserverDeck that establishes the connection between Bpod and Teensy to implement an additional beam break for the observer and check whether the observer leaves its observation d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
2021-07-06 Changed ObserverDeck so that incoming serial events are only processed when they actually arrive; added experiments and sma assembler for the paced task.
2021-07-06 Fixed the video saving location in the labcams call. CAUTION: The current implementation supports only video recording to the saving location of one animal as specified in the first cell of the curre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
2021-07-06 Fixed the psychometric plot to display auditory and multi-sensory performance
2021-07-13 Included the experiment 'ObserverFixationTraining' and associated sma assembler, changed ObserverFigure and chipmunk to retrieve trial information from the observer.
2021-07-21 Added the user input 'cameraSelection' to 'initChipmunk' and calling labcams with the respective cameras allowing the user to specify to record from defined behavioral cameras.
2021-07-30 Added the drawing for the miniscope V4 dummy to the 3d folder.
    [MiniscopeV4Dummy.stl]
2021-08-04 Included a draft for synchronizing trial start and stop TTLs from Bpod with the miniscope sync channel using Teensy.
2021-08-12 Adapted 'synchronizeMiniscopeToBpod.py' to write to correct folder structure and switch counting on Teensy on and off. CAUTION: The execution cannot be terminated with a keyboard interrupt so far and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
2021-08-12 Added a BNC2 pulse as an output action at trial start in the DemonstratorPacedTask sma assembler (for miniscope sync).
2021-08-23 Changed MiniscopeBpodSynchronizer.ino to inserted comma delimited varible names into the header of the mscopelog file.
2021-10-06 Updated parts list.
    [partslist.xlsx]
2021-10-14 Intoduced a pink noise stimulus and a timeout for early withdrawals of the observer during ObserverFixationTraining. This replaces the requirement for the observer to poke into the observer port even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
2021-10-14 Tested last commit and did some bug fixing. Actually, by design of the Teensy implementation, the feedback about trial outcome only comes when the demonstrator's part is over and not immediately.
2021-12-04 Started restructuring 'ObserverFixationSMA' assembler function for a demonstrator-initiated version, added extensive commenting to all the defined states.
2022-01-11 Changed 'ObserverFixationTrainingSMA' to train the observer to only poke once the demonstrator has initiated a trial as evidenced by an auditory cue. Added extensive commenting to each state and incl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
2022-01-12 Modified 'ObserverDeck' to include a condition where the observer does not initiate and teensy reports byte 5 (no initiation). Changed the beam break sensing to an interrupt instead of the constant c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
2022-01-13 Adapted 'ObserverTaskSMA' for the adapted version where the demonstrator initiated. Changed the obsEarlyPunishSound to brown noise to make it more distinguishable from white noise. Introduced a 100 m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
2022-01-13 Bug fixes. Added early withdrawal punishment for the demonstrator while it waits for the observer, changed ObserverDeck on teensy to assume no observer initiation by default.
2022-01-15 Changed 'initChipmunk' and 'chipmunk' to let the user selecta labcams config file instead of the camera. Included a field for specifying the miniscopeID when starting chipmunk.
2022-01-16 Added the sync state to all the sma assemblers for the revised version of chipmunk. During this state the BNC2 output on Bpod will be set to high for 100 ms, which will be logged in the labcams camlo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
2022-01-20 Fixed bug in the demonstrator task and fixation SMA assemblers that immediately advanced to DemonWaitForResponse without waiting until the mouse leaves Port 2.
2022-01-20 Removed outcome delivery to demonstrator in the ObserverFixationTraining SMA. This might be helpful to make the events during the actual observer task more salient. In addition it makes paying attent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
2022-01-29 Inserted a part into 'syncMiniscopeToBpod' that edits a standard miniscope config file according to the information received from the behavior acquistion.
2022-02-01 Introduced a random delay on top of the minObsDur that can maximally be 10% more than set. This is intended to make the fixation duration less predictable and to help the animal to learn that the LED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
2022-02-05 Inserted a small wait time before the loop with the individual trials start. This should ensure that the first frame that labcams is grabbing happens before a trial is started.
2022-04-11 Updated the SMA assembler functions and the figures to incorporate a separate setting for variable virtual observer initiation delays. Move the generation of the task sounds to the main loop because 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
2022-05-23 Introduced a delay in chipmunk when starting the cameras to allow the BlackFly to properly initiate.
2022-06-06 Removed the presentation of the go cue for the virtual demonstrator to make the reward valve click more audible.
2022-08-23 Added updated and corrected versions of the enclosure components.
2023-12-27 Added a state machine assembler to allow the stimulus to continue playing only as long as the mice are poking in the center port.
2025-03-27 Added chipmunk task insertion and inclusion in DecisionTask.
2026-03-17 Modified the Chipmunk schema to also contain the duration of the individual stimulus events and their brightness or loudness. Please note that all of these properties are currently fixed within stim 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
2026-04-07 Added a series of trial parameters to the chipmunk schema that were not yet tracked. Fixed extraction of experimenter and weighting metadata and insertion.
